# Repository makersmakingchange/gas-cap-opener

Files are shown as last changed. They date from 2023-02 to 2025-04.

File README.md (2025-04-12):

# Gas Cap Opener
The gas cap opener is a device designed to allow users with limited grip strength and hand function to easily open and close the gas cap on their vehicle.

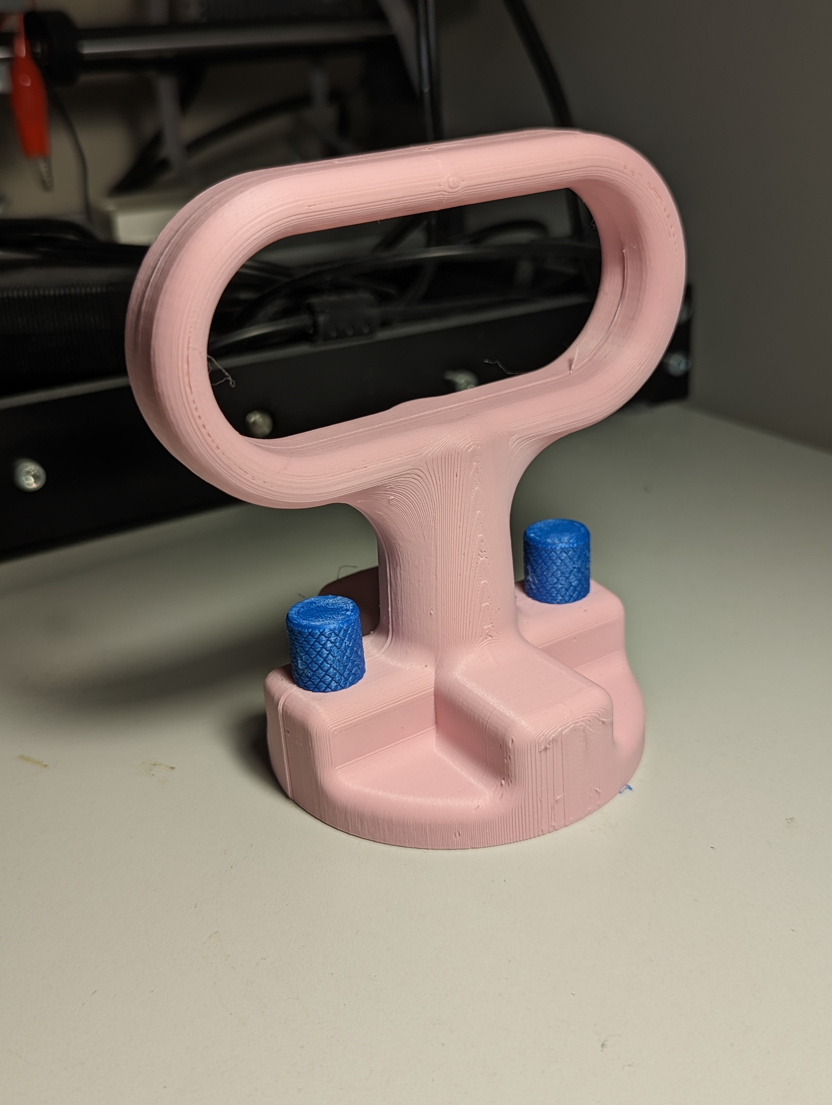
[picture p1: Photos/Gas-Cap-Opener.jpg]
Picture of Gas Cap Opener.


## More info at
- [Makers Making Change Project Page](https://makersmakingchange.com/project/gas-cap-opener/)

## How to Obtain a Gas Cap Opener
### 1. Do it Yourself (DIY) or Do it Together (DIT)

This is an open-source assistive technology, so anyone is free to build it. All of the files and instructions required to build the Gas Cap Opener are contained within this repository. Refer to the Maker Checklist below.

### 2. Request a build of this device

If you would like to obtain a Gas Cap Opener , you may submit a build request through the [MMC Library Page](https://makersmakingchange.com/project/gas-cap-opener/). The requestor is responsible for the cost of materials and any shipping.

### 3. How to build this device for someone else

If you have the skills and equipment to build this device, and would like to donate your time to create the switch for someone who needs it, visit the [MMC Maker Wanted](https://makersmakingchange.com/maker-wanted/) section.

## Getting Started

### 1. Read the Makers Checklist

The Makers Checklist 

### 2. Order the Off-The-Shelf Components

The [Bill of Materials](/Documentation/Gas_Cap_Opener_BOM_V1.0.xlsx) lists all of the parts and components required to build the Gas Cap Opener. 

### 3. Print the 3D Printable components

All of the files and individual print files can be in the [/Build_Files/3D_Printing_Files](/Build_Files/3D_Printing_Files/) folder.

### 4. Assemble the Gas Cap Opener

Reference the [Assembly Guide](/Documentation/Gas_Cap_Opener_Assembly_Guide_V1.0.pdf) for the tools and steps required to build each portion.

## Files
### Documentation
| Document             | Version | Link |
|----------------------|---------|------|
| Design Rationale     | 1.0     | [Gas_Cap_Opener_Design_Rationale](/Documentation/Gas_Cap_Opener_Design_Rationale_V1.0.pdf)     |
| Maker Checklist      | 1.0     | [Gas_Cap_Opener_Maker_Checklist](/Documentation/Gas_Cap_Opener_Maker_Checklist_V1.0.pdf)     |
| Bill of Materials    | 1.0     | [Gas_Cap_Opener_Bill_of_Materials](/Documentation/Gas_Cap_Opener_BOM_V1.0.xlsx)     |
| 3D Printing Guide    | 1.0     | [Gas_Cap_Opener_3D_Printing_Guide](/Documentation/Gas_Cap_Opener_3D_Printing_Guide_V1.0.pdf)     |
| Assembly Guide       | 1.0     | [Gas_Cap_Opener_Assembly_Guide](/Documentation/Gas_Cap_Opener_Assembly_Guide_V1.0.pdf)     |
| User Guide           | 1.0     | [Gas_Cap_Opener_User_Guide](/Documentation/Gas_Cap_Opener_User_Guide_V1.0.pdf)    |
| Changelog            | 1.0     | [Gas_Cap_Opener_Changelog](/Documentation/Gas_Cap_Opener_Changelog_V1.0.pdf)     |

### Design Files
[CAD Files](/Design_Files)

### Build Files
 - [3D Printing Files](/Build_Files/3D_Printing_Files)

## Attribution
Designers:
 - Design and Documentation by Neil Squire Society/Makers Making Change

## License
Everything needed or used to design, make, test, or prepare the Gas Cap Opener is licensed under the [Attribution-NonCommercial-ShareAlike 4.0 ](https://creativecommons.org/licenses/by-nc-sa/4.0/).

Accompanying material such as instruction manuals, videos, and other copyrightable works that are useful but not necessary to design, make, test, or prepare the <Device-Name> are published under a Creative Commons Attribution-ShareAlike 4.0 license https://creativecommons.org/licenses/by-sa/4.0/ (CC BY-SA 4.0).

---
<!-- ABOUT MMC START -->
## About Makers Making Change
[Makers Making Change Logo](https://www.makersmakingchange.com/)

Makers Making Change is a program of [Neil Squire](https://www.neilsquire.ca/), a Canadian non-profit that uses technology, knowledge, and passion to empower people with disabilities.

Makers Making Change leverages the capacity of community based Makers, Disability Professionals and Volunteers to develop and deliver affordable Open Source Assistive Technologies.

 - Website: [www.MakersMakingChange.com](https://www.makersmakingchange.com/)
 - GitHub: [makersmakingchange](https://github.com/makersmakingchange)
 - Bluesky: [@makersmakingchange.bsky.social](https://bsky.app/profile/makersmakingchange.bsky.social)
 - Instagram: [@makersmakingchange](https://www.instagram.com/makersmakingchange)
 - Facebook: [makersmakechange](https://www.facebook.com/makersmakechange)
 - LinkedIn: [Neil Squire Society](https://www.linkedin.com/company/neil-squire-society/)
 - Thingiverse: [makersmakingchange](https://www.thingiverse.com/makersmakingchange/about)
 - Printables: [MakersMakingChange](https://www.printables.com/@MakersMakingChange)

### Contact Us
For technical questions, to get involved, or to share your experience we encourage you to [visit our website](https://www.makersmakingchange.com/) or [contact us](https://www.makersmakingchange.com/s/contact).
<!-- ABOUT MMC END -->

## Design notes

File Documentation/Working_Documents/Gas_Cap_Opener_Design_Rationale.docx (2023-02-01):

# Introduction

Some people with limited grip strength/limited hand function may have difficulty opening the gas cap on their vehicle. There are several commercial and DIY options available for opening vehicle gas caps, but most designs focus on users with limited grip strength, leaving few options available for users with limited hand function.

# Research

Commercial
Name | Picture | Price | Link

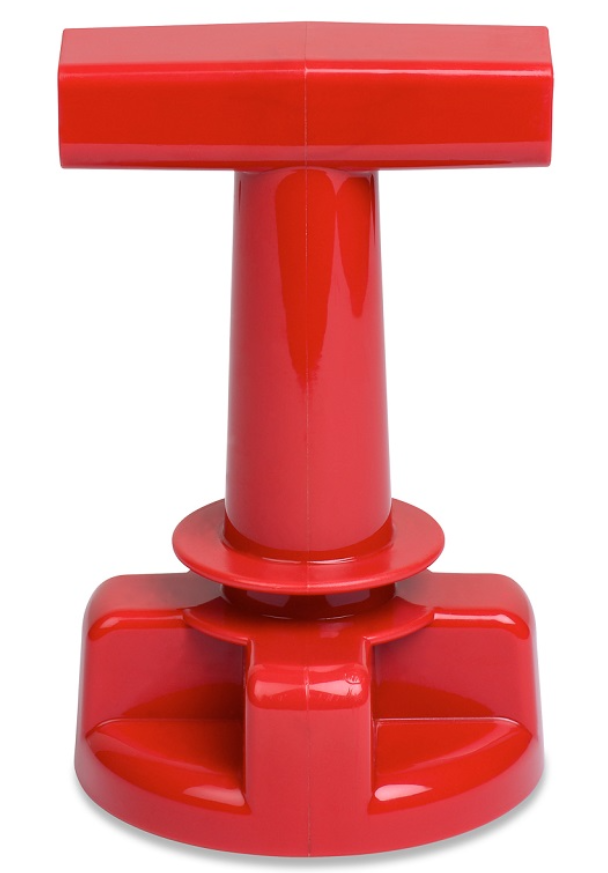
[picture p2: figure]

Freedom Gas Cap Wrench | | $17.95 | Link (https://www.arthritissupplies.com/gas-cap-wrench.html)

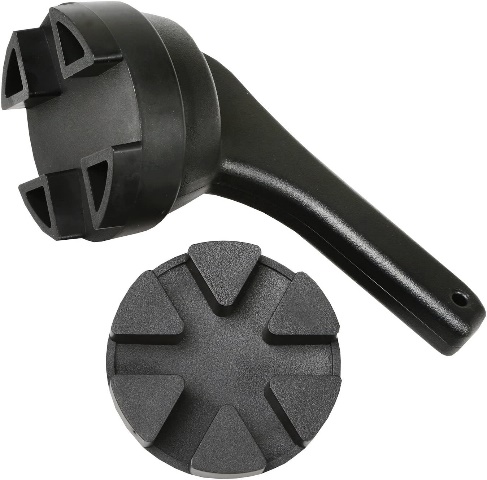
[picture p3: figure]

Bandwagon Gas Cap Aid | | $32.11 | Link (https://www.amazon.ca/BW-BRANDS-9270-Bandwagon-Gas/dp/B072WC9MVF?hvadid=459470168074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)

DIY
Name | Picture | Price | Link

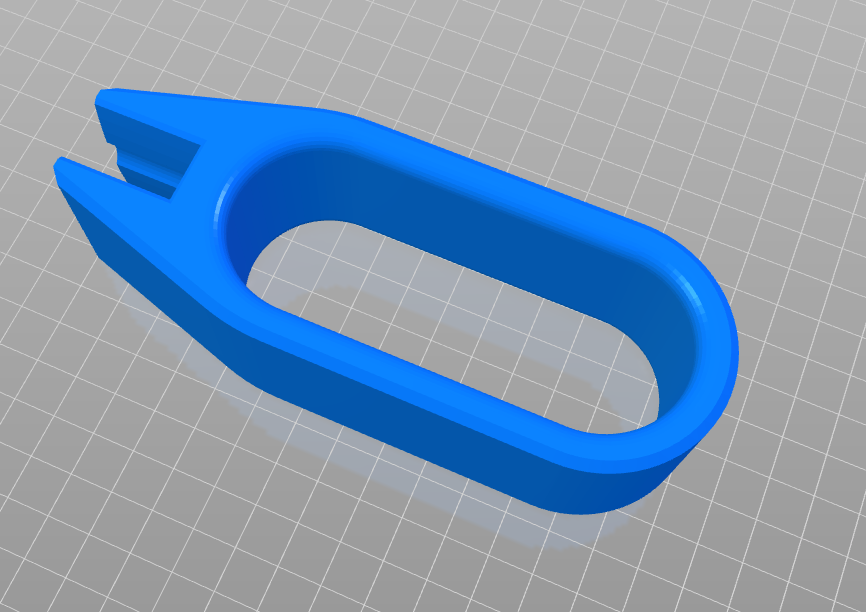
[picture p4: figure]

Gas Cap opener | | N/A | Link (https://www.thingiverse.com/thing:4707409)

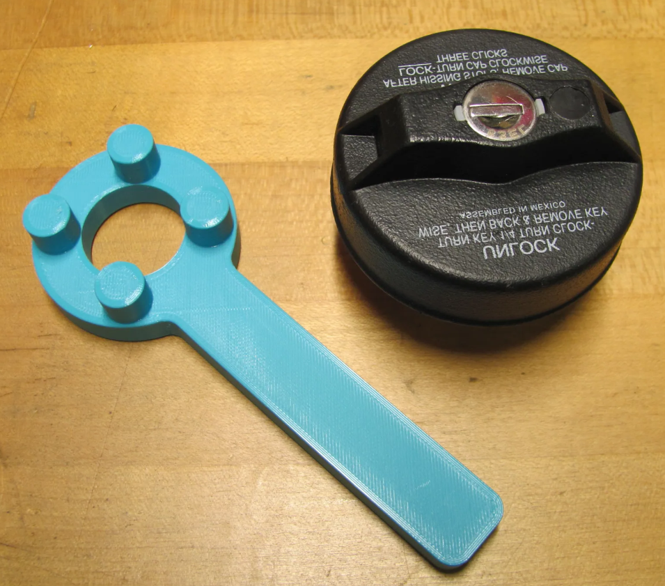
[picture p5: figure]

RV Locking Gas Cap Wrench | | N/A | Link (https://www.printables.com/model/64304-rv-locking-gas-cap-wrench)

# Requirements

## Goals

G01 | To allow users with limited hand function to remove and replace the gas cap on their vehicle

## Functional Requirements

F01 | Device must open and tighten the gas cap on any passenger vehicle
F02 | Device must be usable by users with limited hand function

## Non-functional Requirement

NF01 | Each component printable in less than 8 hours
NF02 | Device must be printable with minimum supports

## Constraints

C01 | Built with 3D printable and off the shelf components

# Prototyping

The initial concept was inspired by the Freedom Gas Cap Wrench. Each round of testing identified a new flaw in the design, and a new prototype was created.

# Testing

The initial prototype was tested on a Toyota Rav4. It removed the gas cap of the vehicle, but the handle was found to be uncomfortable and difficult to grip. Additionally, the bolt attachment points had to be removed for it to fit into the gas cap cavity.

The handle was redesigned along with the new bolt attachment points, and it was tested again on a Rav4 and a Toyota Corolla. This time it was able to remove the gas cap on the Rav4, but it did not fit over the gas cap on the Corolla. The edges were found to catch onto the strap holding the cap to the car.

The width of the gas cap slot was increased for the next prototype, and a chamfer added around the outer ring.

For the final version, the bolts were replaced with 3D printed pins and nuts.

# Opportunities for Improvement

- The device could be redesigned to eliminate printing supports

© 2023 by Neil Squire. This work is licensed under the CC BY SA 4.0 License: http://creativecommons.org/licenses/by-sa/4.0 Files available at https://makersmakingchange.com/project/gas-cap-opener/ Page 2 of 2

V1.0 | January 2023 Gas Cap Opener Design Rationale

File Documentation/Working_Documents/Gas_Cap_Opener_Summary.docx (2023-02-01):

# Title

Gas Cap Opener

## Subtitle

The gas cap opener is a device designed to allow users with limited grip strength and hand function to easily open and close the gas cap on their vehicle.

## Device Details

### Overview

Some people with limited grip strength/hand function have difficulty opening the gas cap on their vehicle. There are several commercial and DIY options available for opening vehicle gas caps, but most focus on grip strength issues, with limited options available for users with limited hand function.

### Usage

To use, place the + shaped end of the gas cap opener over the gas cap on the car. The handle on the opener can then be turned to either tighten or loosen the cap, as normal.

If this device does not function with the gas cap on your vehicle, please get in touch with us so we can make changes to the design to make it compatible with more vehicles.

### Cost

<$10

### Build Instructions

This device is assembled from two separate halves, connected by an aligning pin and two threaded knobs.

#### Skills Required

- 3D Printing

#### Time Required

- 3D printing time: 884 min
- Assembly Time: 5 min

#### Tools

- 3D Printer
- Pliers

#### Components

- Handle x2
- Knob x2
- Pin x1

#### Attribution

Design by Neil Squire Society/Makers Making Change

Initial prototype inspired by the Freedom Gas Cap Wrench

© 2023 by Neil Squire. This work is licensed under the CC BY SA 4.0 License: http://creativecommons.org/licenses/by-sa/4.0 Files available at https://makersmakingchange.com/project/gas-cap-opener/ Page 2 of 2

V1.0 | January 2023 Gas Cap Opener Summary

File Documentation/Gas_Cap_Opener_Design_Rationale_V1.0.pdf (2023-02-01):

V1.0 | January 2023

## Gas Cap Opener

## DESIGN RATIONALE

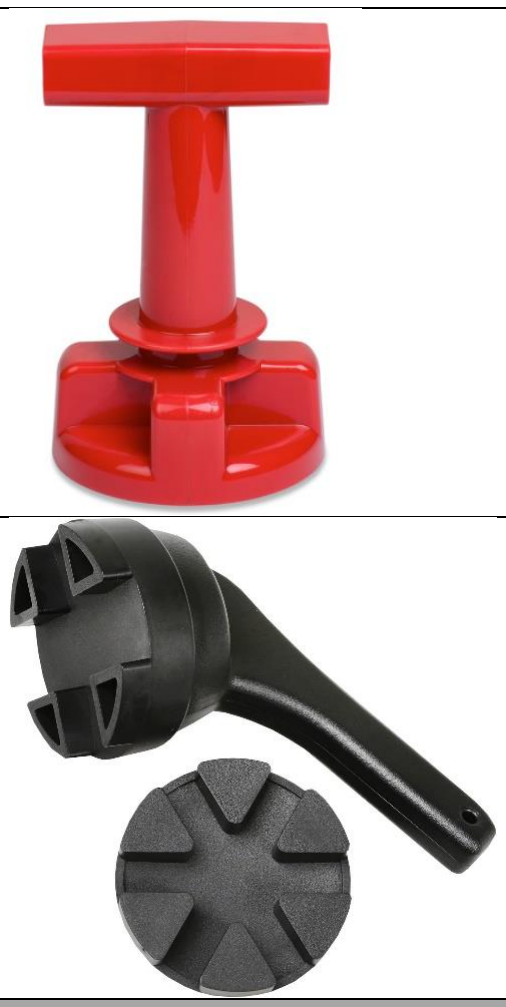
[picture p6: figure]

© 2023 by Neil Squire. (https://neilsquire.ca/)
This work is licensed under the CC BY SA 4.0 License: http://creativecommons.org/licenses/by-sa/4.0
Files available at https://makersmakingchange.com/project/gas-cap-opener/ | Page 1 of 3

### Introduction

Some people with limited grip strength/limited hand function may have difficulty opening the gas cap on their vehicle. There are several commercial and DIY options available for opening vehicle gas caps, but most designs focus on users with limited grip strength, leaving few options available for users with limited hand function.

### Research

Commercial
Name | Picture | Price | Link
Freedom Gas Cap Wrench | | $17.95 | Link (https://www.arthritissupplies.com/gas-cap-wrench.html)
Bandwagon Gas Cap Aid | | $32.11 | Link (https://www.amazon.ca/BW-BRANDS-9270-Bandwagon-Gas/dp/B072WC9MVF?hvadid=459470168074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)

DIY
Name | Picture | Price | Link

## DESIGN RATIONALE

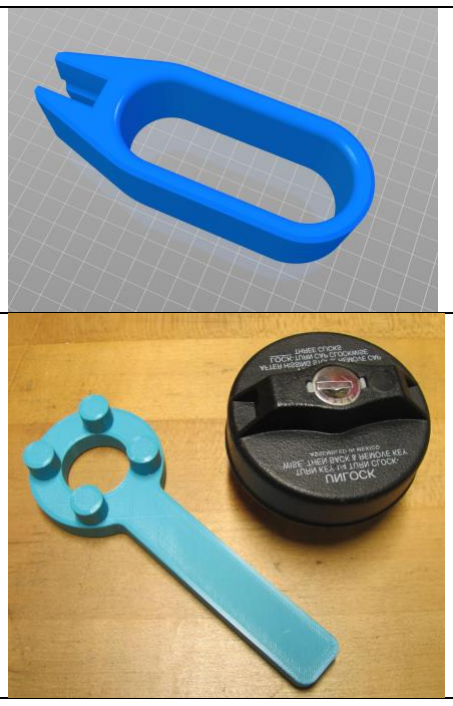
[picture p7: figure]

Files available at https://makersmakingchange.com/project/gas-cap-opener/ | Page 2 of 3
Gas Cap opener | N/A | Link (https://www.thingiverse.com/thing:4707409)
RV Locking Gas Cap Wrench | N/A | Link (https://www.printables.com/model/64304-rv-locking-gas-cap-wrench)

### Requirements

### Goals

G01 To allow users with limited hand function to remove and replace the gas cap on their vehicle

### Functional Requirements

F01 | Device must open and tighten the gas cap on any passenger vehicle
F02 | Device must be usable by users with limited hand function

### Non-functional Requirement

NF01 | Each component printable in less than 8 hours
NF02 | Device must be printable with minimum supports

### Constraints

C01 Built with 3D printable and off the shelf components

## DESIGN RATIONALE

Files available at https://makersmakingchange.com/project/gas-cap-opener/ | Page 3 of 3

### Prototyping

The initial concept was inspired by the Freedom Gas Cap Wrench. Each round of testing identified a new flaw in the design, and a new prototype was created.

### Testing

The initial prototype was tested on a Toyota Rav4. It removed the gas cap of the vehicle, but the handle was found to be uncomfortable and difficult to grip. Additionally, the bolt attachment points had to be removed for it to fit into the gas cap cavity.

The handle was redesigned along with the new bolt attachment points, and it was tested again on a Rav4 and a Toyota Corolla. This time it was able to remove the gas cap on the Rav4, but it did not fit over the gas cap on the Corolla. The edges were found to catch onto the strap holding the cap to the car.

The width of the gas cap slot was increased for the next prototype, and a chamfer added around the outer ring.

For the final version, the bolts were replaced with 3D printed pins and nuts.

### Opportunities for Improvement

- The device could be redesigned to eliminate printing supports

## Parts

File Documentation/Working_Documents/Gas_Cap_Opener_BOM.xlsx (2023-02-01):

Device: Gas Cap Opener |  | Total Cost | Total Print time (hr) | Total filament (g)
Version: V1.0 | Date Created: 1/10/2023 | $2.48 | 7.57 | 99
Commercial Parts:
Part type (Electrical. Mechanical, Sanitization, ect) | Part Name | Quantity Needed | Pkg Quantity | Price per package | Price per Unit | Price for qty needed | Link
 |  |  |  |  |  | $0.00 | https://www.homedepot.ca/product/paulin-1-4-x-1-inch-flat-head-square-drive-stove-bolt-with-nut-zinc-plated-10-pcs/1000122118
 |  |  |  |  |  | $0.00 | https://www.homedepot.ca/product/paulin-1-4-20-inch-finished-hex-nut-grade-2-oversized-hot-dipped-galvanized-unc/1000141150
3D Printed Parts ESTIMATED PRICING USING 1KG ROLL COST: | $25.00
Part | Description | Quantity Needed | TOTAL Mass (g) | Estimated Price | Print Time (Min) | Link
Handle | Main handle body | 2 | 94 | $2.35 | 424
Knob | Threaded knob | 2 | 4 | $0.10 | 20
Pin | Aligning pin | 1 | 1 | $0.03 | 10
 |  |  |  | $0.00
 |  |  |  | $0.00
 |  |  | Total Print Cost: | $2.48
Tools for Assembly
Pliers
Alternatives (if there are other sources for some parts link them below)
Part and description | Link

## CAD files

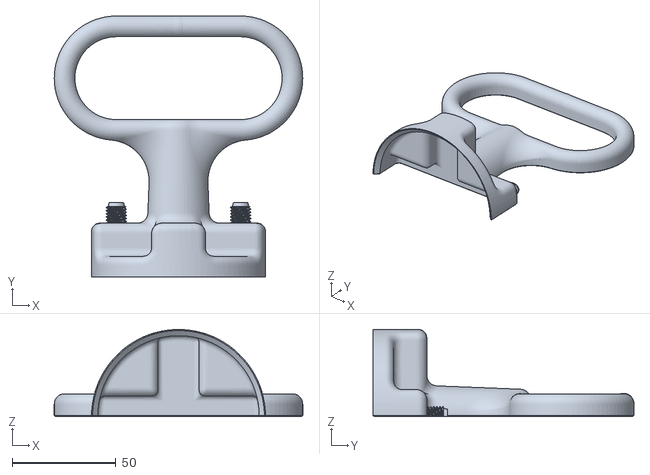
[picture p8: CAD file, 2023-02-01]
Build_Files/3D_Printing_Files/Handle.stl
120.0 x 126.0 x 42.0

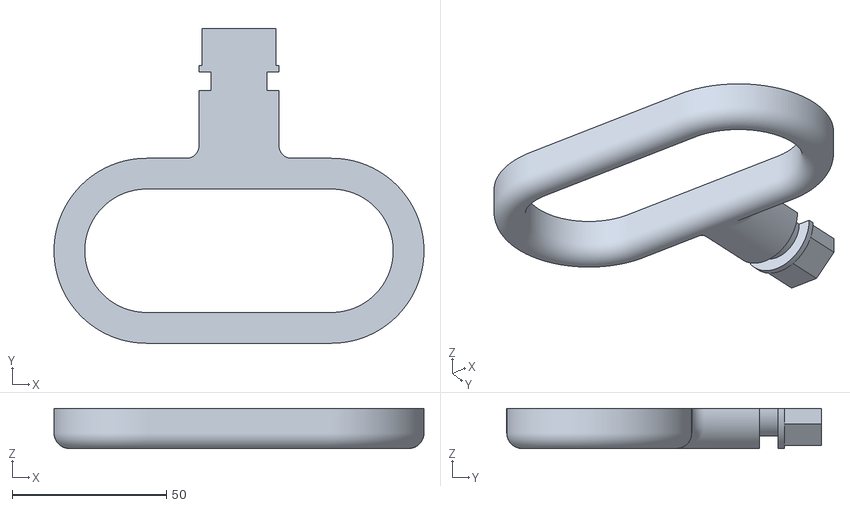
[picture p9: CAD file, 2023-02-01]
Threaded_Variant/Gas_Cap_Opener_Thread_Gas_Cap_Opener_Thread v3_Handle_1_Handle1.stl
120.0 x 102.0 x 13.0

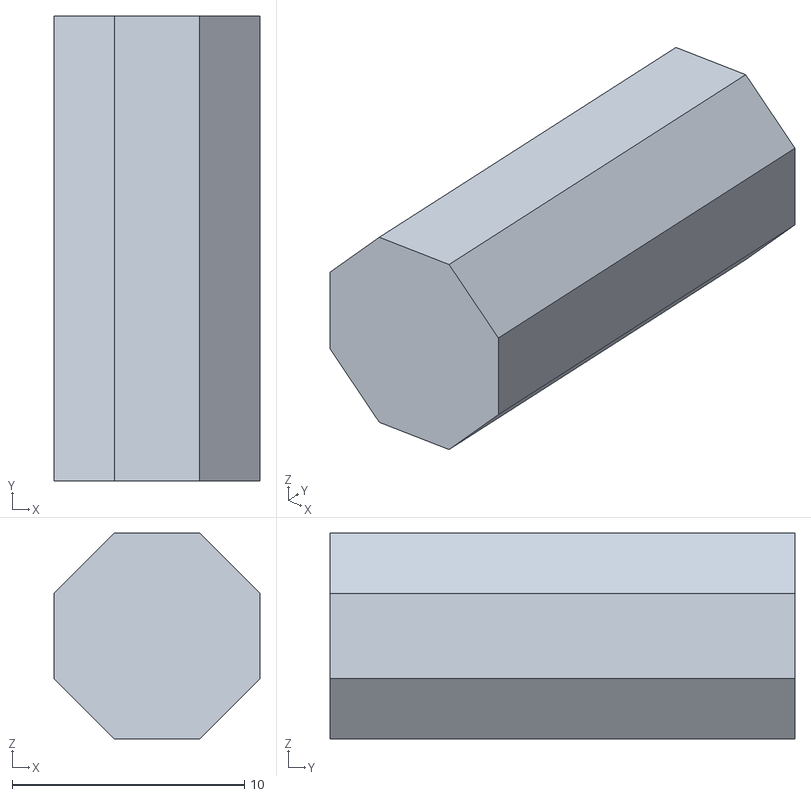
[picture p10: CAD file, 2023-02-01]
Build_Files/3D_Printing_Files/Pin.stl
8.87 x 20.0 x 8.87

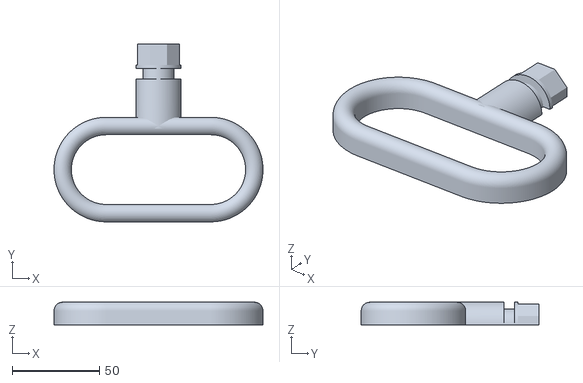
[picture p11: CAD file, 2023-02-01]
Threaded_Variant/Gas_Cap_Opener_Thread_Gas_Cap_Opener_Thread v1_Handle_1_Handle2.stl
120.0 x 102.0 x 13.0

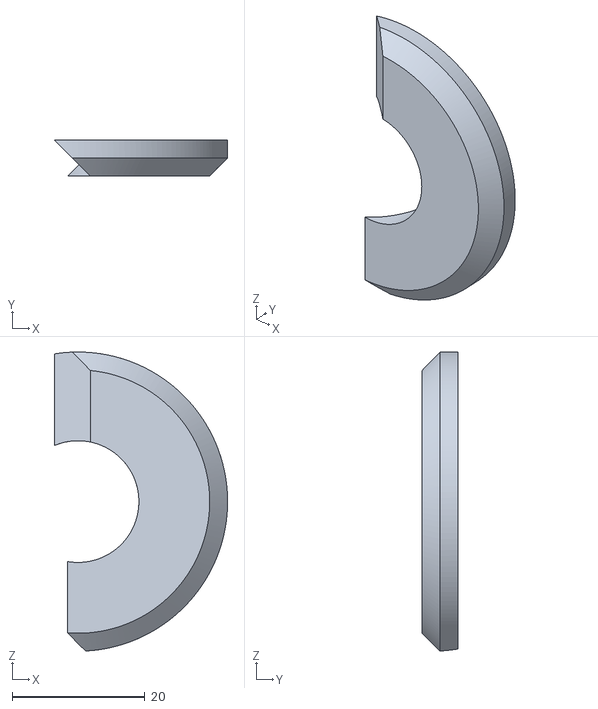
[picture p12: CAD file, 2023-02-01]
Threaded_Variant/Gas_Cap_Opener_Thread_Gas_Cap_Opener_Thread v1_Component6_1_Clip2.stl
26.1 x 5.40 x 45.0

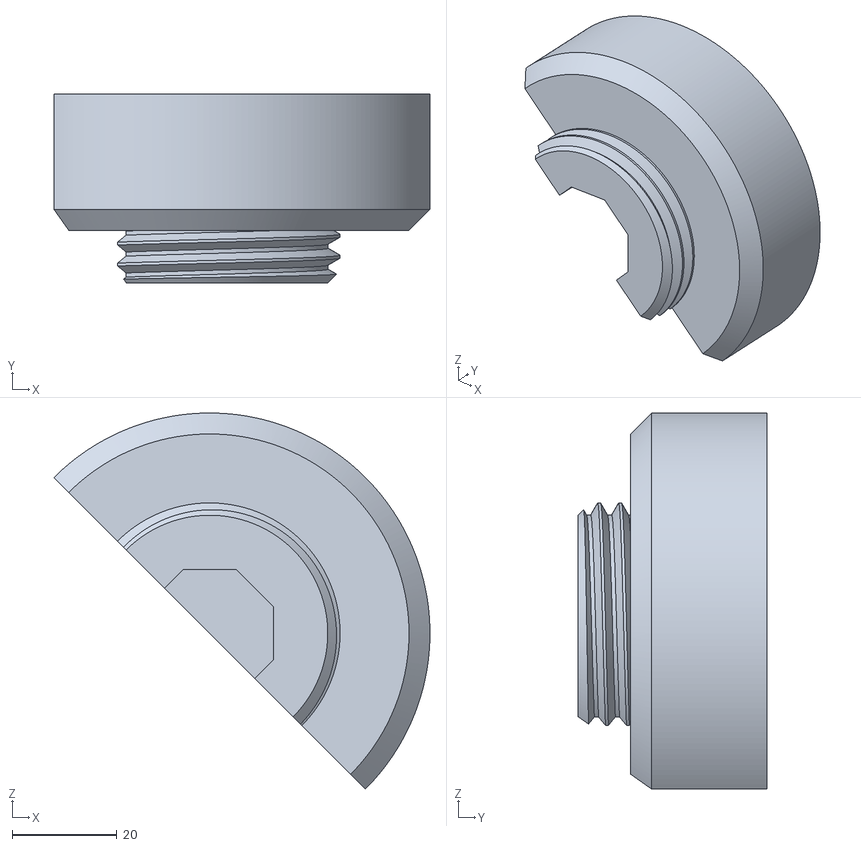
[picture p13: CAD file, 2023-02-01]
Threaded_Variant/Gas_Cap_Opener_Thread_Gas_Cap_Opener_Thread v3_Cap2.stl
71.7 x 36.0 x 71.7

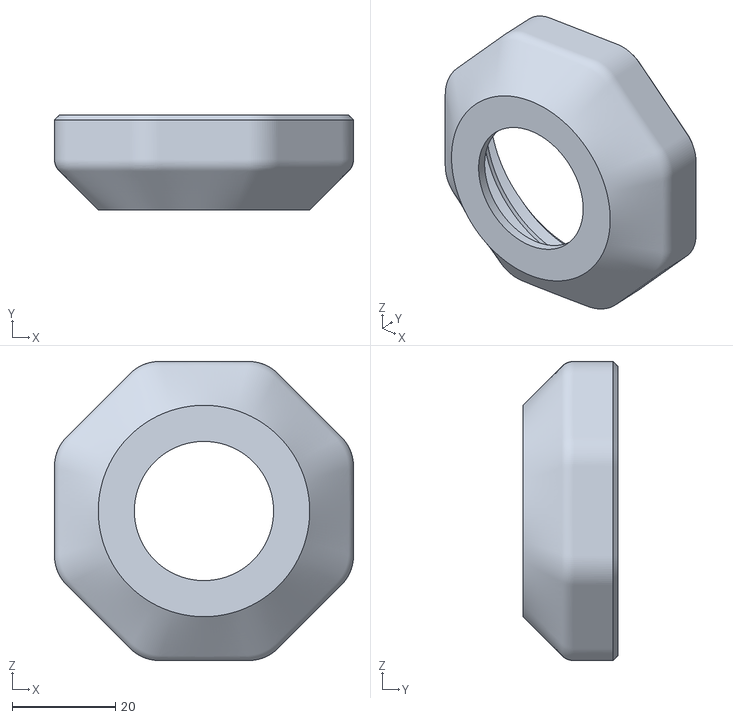
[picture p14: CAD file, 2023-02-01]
Threaded_Variant/Gas_Cap_Opener_Thread_Gas_Cap_Opener_Thread v3_Nut_1_Nut.stl
58.0 x 18.5 x 58.0

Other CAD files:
Threaded_Variant/Gas_Cap_Opener_Thread_Gas_Cap_Opener_Thread v1_Cap2.stl
Threaded_Variant/Gas_Cap_Opener_Thread_Gas_Cap_Opener_Thread v1_Handle_1_Handle1.stl
Threaded_Variant/Gas_Cap_Opener_Thread_Gas_Cap_Opener_Thread v1_Component5_1_Clip1.stl
Threaded_Variant/Gas_Cap_Opener_Thread_Gas_Cap_Opener_Thread v3_Cap1.stl
Threaded_Variant/Gas_Cap_Opener_Thread_Gas_Cap_Opener_Thread v1_Cap1.stl
Threaded_Variant/Gas_Cap_Opener_Thread_Gas_Cap_Opener_Thread v3_Component5_1_Clip1.stl
Threaded_Variant/Gas_Cap_Opener_Thread_Gas_Cap_Opener_Thread v3_Handle_1_Handle2.stl
Design_Files/Gas Cap Opener Finalized v4.f3d

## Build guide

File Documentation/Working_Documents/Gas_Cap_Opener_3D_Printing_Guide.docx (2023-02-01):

# 3D Printing Summary

Metrics | Configuration 1
Total Print Time (min) | 884
Total Number of Components | 5
Typical Total Mass (g) | 99
Typical Number of Print Setups | 3

# 3D Printing Settings

Print File Name | Qty | Total Print Time (hr:min) | Mass (g) | Infill (%) | Support(Y/N) | Layer Height/ Nozzle Diameter(mm) | Notes (orientation, special settings, etc.)
Handle.stl | 2 | 6:32 | 47 | 20 | Y | 0.2/0.4 | - Requires support - Print in orientation given in STL
Knob.stl | 2 | 0:20 | 2 | 20 | N | 0.2/0.4 | - Print in orientation given in STL
Pin.stl | 1 | 0:10 | 1 | 20 | N | 0.2/0.4 | - Print in orientation given in STL

# Customization Options

- The device can be printed in any colour that the user wants

# Post-Processing

- Remove all supports from the handle pieces
- Use a hobby knife and sandpaper to remove any rough edges

# Examples of Quality Prints

Photos of Handle

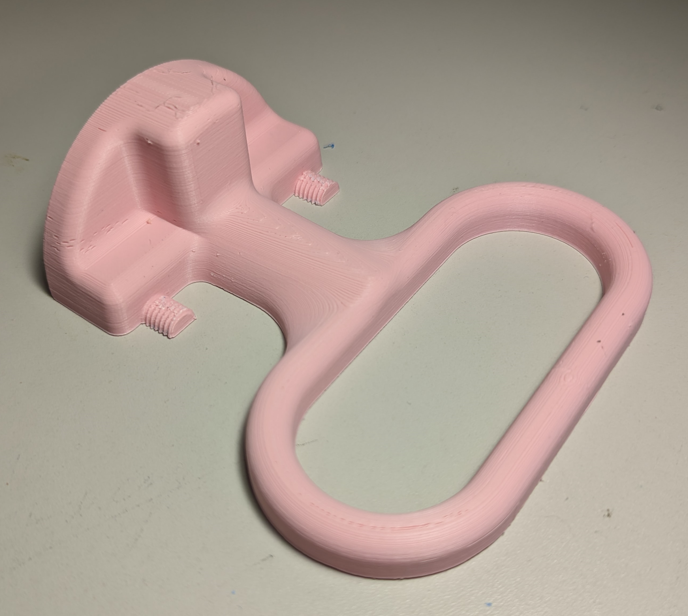
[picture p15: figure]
Top view of handle
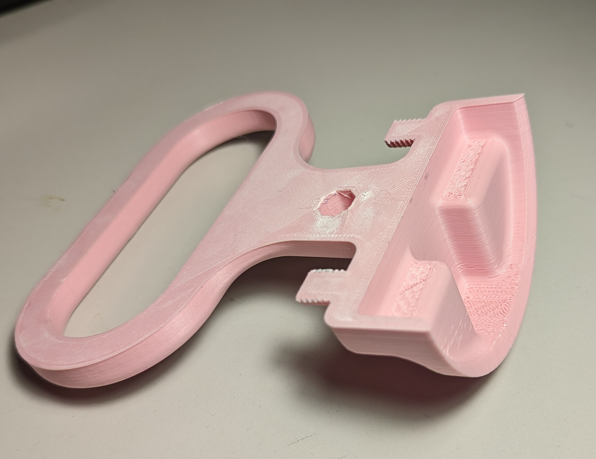
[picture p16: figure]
Bottom view of handle

Photos of Knob

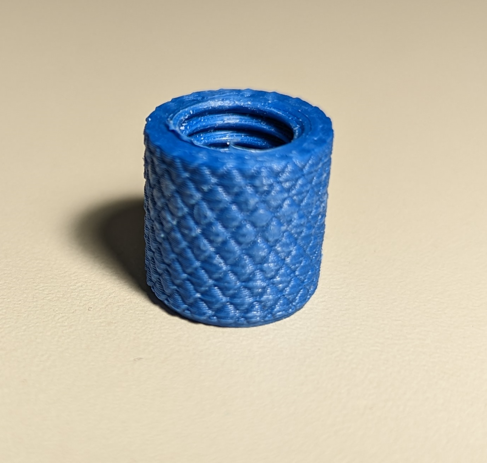
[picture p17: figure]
knob

Photos of Pin

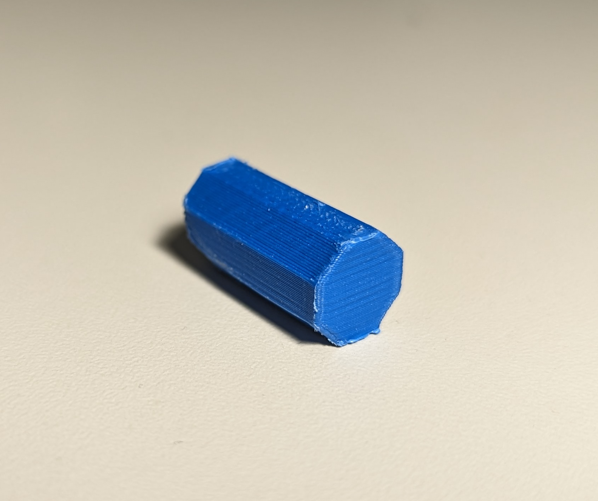
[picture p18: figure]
Octagonal pin

© 2023 by Neil Squire. This work is licensed under the CC BY SA 4.0 License: http://creativecommons.org/licenses/by-sa/4.0 Files available at https://makersmakingchange.com/project/gas-cap-opener/ Page 2 of 2

V1.0 | January 2023 Gas Cap Opener 3D Printing Guide

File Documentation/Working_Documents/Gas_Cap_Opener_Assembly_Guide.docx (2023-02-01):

# Required Components

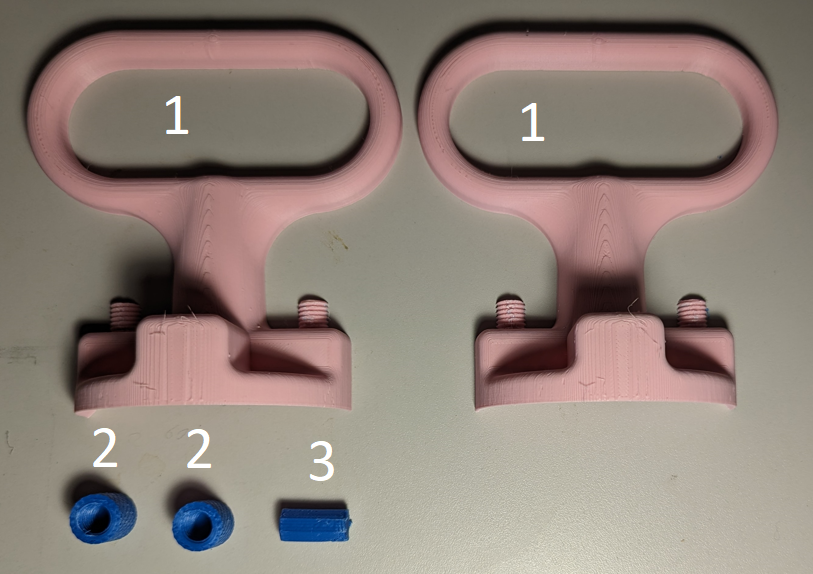
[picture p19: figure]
All the parts for the Gas Cap Opener laid out and numbered

| BOM 1. Handle X2 2. Knob X2 3. Pin

# Required Tools

- Pliers

# Required Personal Protective Equipment (PPE)

- Eye protection

# Assembly Instructions

## Step 1

Insert the octagonal pin into matching slot on one side of the handle.

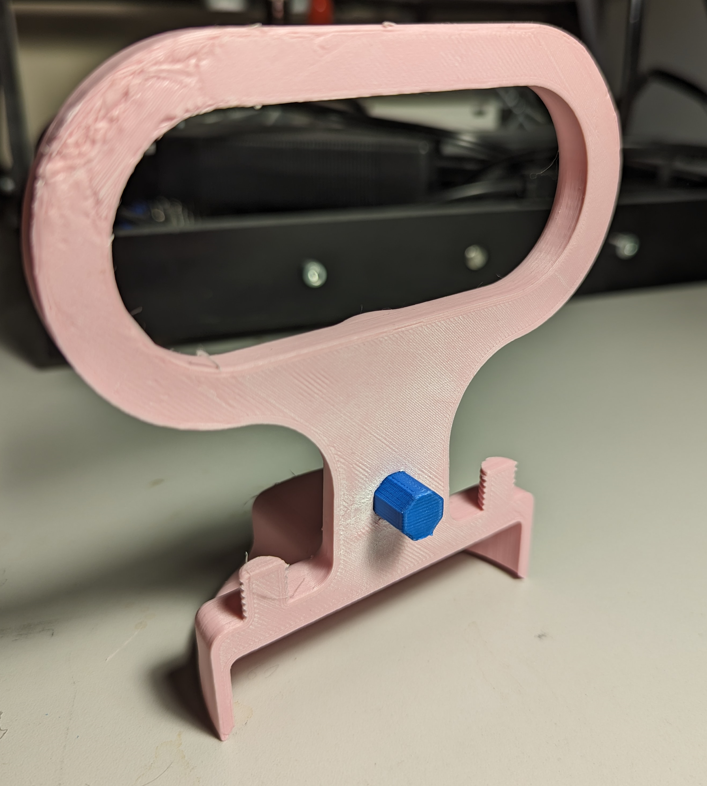
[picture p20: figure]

## Step 2

Align the octagonal hole on the second handle with the pin and press them together.

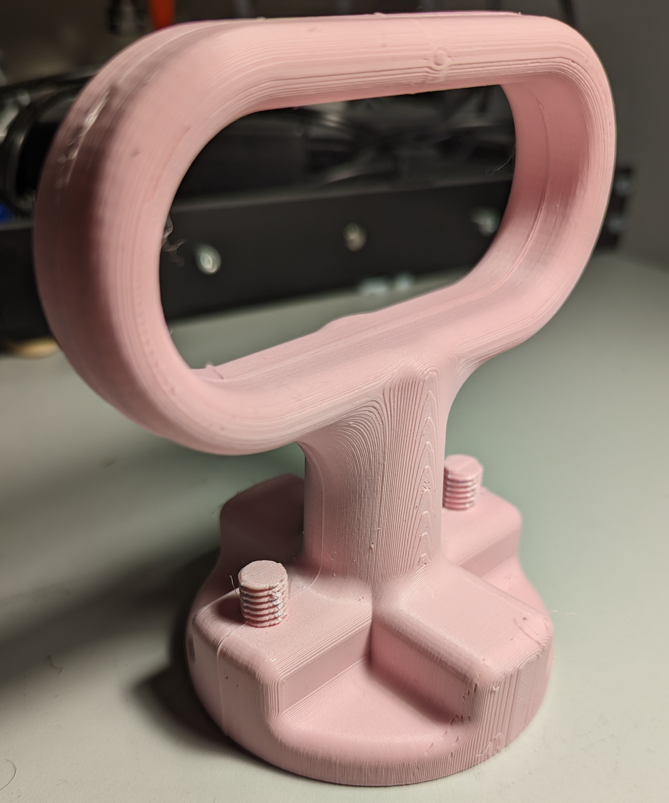
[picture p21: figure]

## Step 3

Screw the knobs onto the threads on the handle. You may need to twist the handle slightly to align the threads. The knob will be tight, and a pair of pliers can be used to fully tighten them.

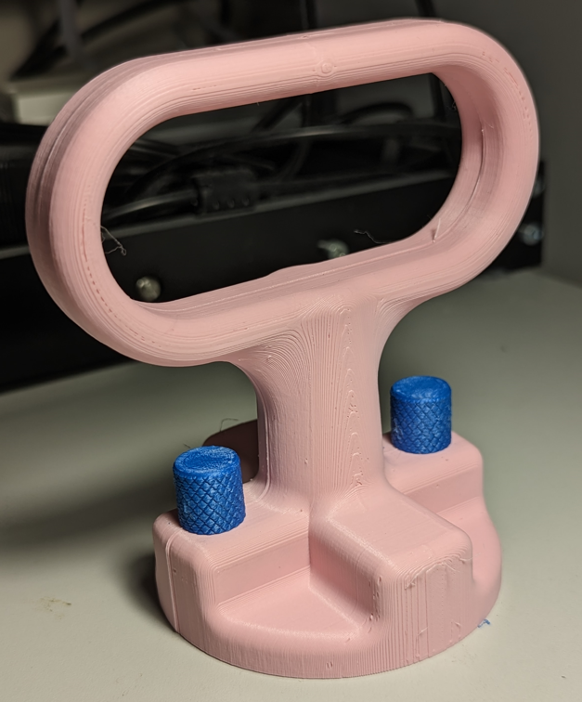
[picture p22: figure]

© 2023 by Neil Squire. This work is licensed under the CC BY SA 4.0 License: http://creativecommons.org/licenses/by-sa/4.0 Files available at https://makersmakingchange.com/project/gas-cap-opener/ Page 2 of 2

V1.0 | January 2023 Gas Cap Opener Assembly Guide

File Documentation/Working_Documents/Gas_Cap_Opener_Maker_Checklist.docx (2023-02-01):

# Maker To Do List

- Read through the Assembly Guide to become familiar with required components, tools, supplies, and safety gear and overall assembly steps.
- Talk to User about customization options (e.g., color, any special requests, etc.)
- Order hardware components
- Gather tools, supplies, and safety equipment.
- Assemble the device
- Test device
- Print “User Quick Guide”

# Items to Give to User

- Assembled, tested device
- “User Quick Guide”

© 2023 by Neil Squire. This work is licensed under the CC BY SA 4.0 License: http://creativecommons.org/licenses/by-sa/4.0 Files available at https://makersmakingchange.com/project/gas-cap-opener/ Page 2 of 2

V1.0 | January 2023 Gas Cap Opener Maker Checklist

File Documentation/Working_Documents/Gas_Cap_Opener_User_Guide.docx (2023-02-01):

## Introduction

Some people with limited grip strength/limited hand function have difficulty opening the gas cap on their vehicle. There are several commercial and DIY options available for opening vehicle gas caps, but most focus on grip strength issues, with limited options available for users with limited hand function.

## Features

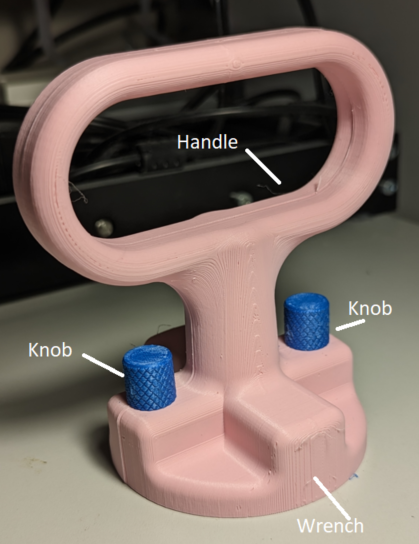
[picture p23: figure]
Annotated picture of the wrench

## Usage

To use, place the + shaped end of the gas cap opener over the gas cap on the car. The handle on the opener can then be turned to either tighten or loosen the cap, as normal.

## Compatibility

The gas cap opener is compatible with every gas cap with a handle width of less than 2cm and a length of less than 8cm.

## Specifications

The handle is 5cm by 10cm, the overall device is 12.5cm tall, and has a wrench diameter of 8.5 cm.

The device weighs 70g

## Cleaning

Wipe device clean with damp cloth.

© 2023 by Neil Squire. This work is licensed under the CC BY SA 4.0 License: http://creativecommons.org/licenses/by-sa/4.0 Files available at https://makersmakingchange.com/project/gas-cap-opener/ Page 2 of 3

V1.0 | January 2023 Gas Cap Opener user Quick Guide

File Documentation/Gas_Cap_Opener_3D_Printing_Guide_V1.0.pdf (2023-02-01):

V1.0 | January 2023

## Gas Cap Opener

## 3D PRINTING GUIDE

© 2023 by Neil Squire. (https://neilsquire.ca/)
This work is licensed under the CC BY SA 4.0 License: http://creativecommons.org/licenses/by-sa/4.0
Files available at https://makersmakingchange.com/project/gas-cap-opener/ | Page 1 of 3

### 3D Printing Summary

Metrics | Configuration 1
Total Print Time (min) | 884
Total Number of Components | 5
Typical Total Mass (g) | 99
Typical Number of Print Setups | 3

### 3D Printing Settings

Print File Name | Qty | Total Print Time (hr:min) | Mass (g) | Infill (%) | Support(Y/N) | Layer Height/ Nozzle Diameter(mm) | Notes (orientation, special settings, etc.)
Handle.stl | 2 | 6:32 | 47 | 20 | Y | 0.2/0.4 | -Requires support - Print in orientation given in STL
Knob.stl | 2 | 0:20 | 2 | 20 | N | 0.2/0.4 | -Print in orientation given in STL
Pin.stl | 1 | 0:10 | 1 | 20 | N | 0.2/0.4 | -Print in orientation given in STL

### Customization Options

- The device can be printed in any colour that the user wants

### Post-Processing

- Remove all supports from the handle pieces
- Use a hobby knife and sandpaper to remove any rough edges

## 3D PRINTING GUIDE

### Examples of Quality Prints

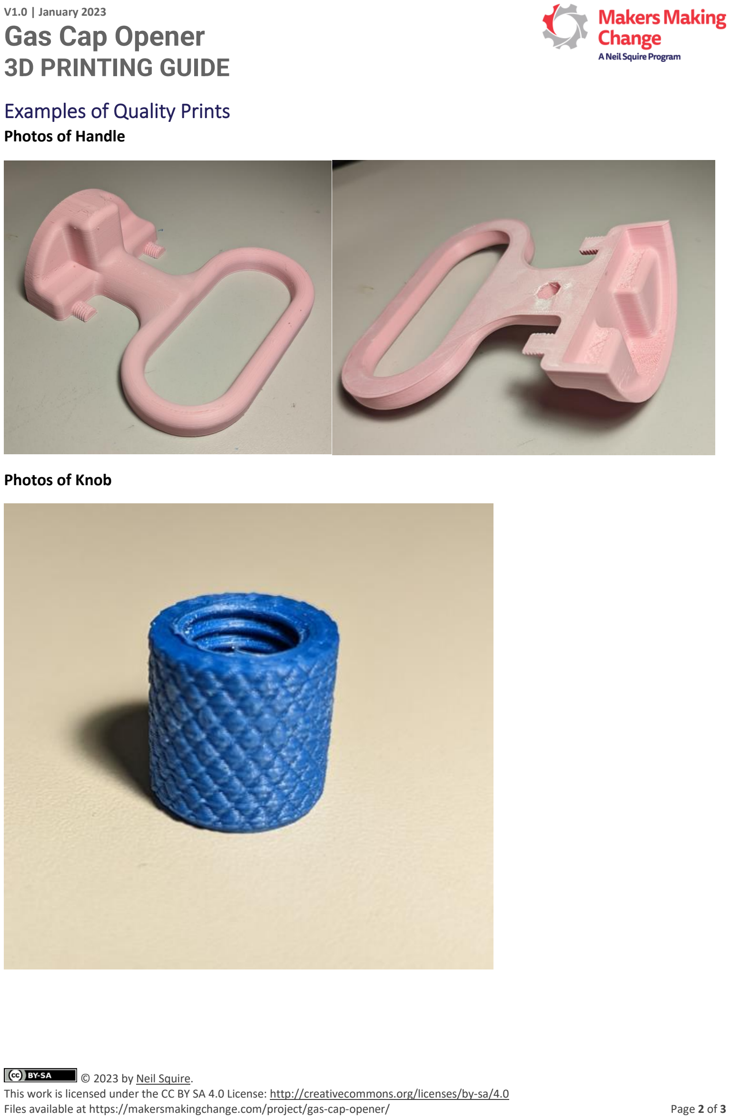
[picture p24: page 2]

Files available at https://makersmakingchange.com/project/gas-cap-opener/ | Page 2 of 3

Photos of Handle

Photos of Knob

## 3D PRINTING GUIDE

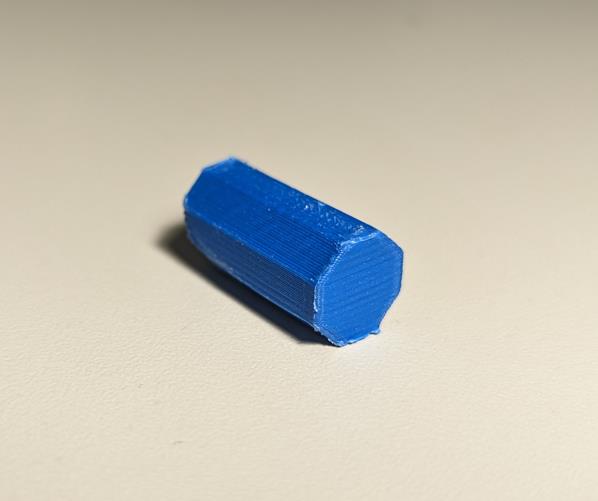
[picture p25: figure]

Files available at https://makersmakingchange.com/project/gas-cap-opener/ | Page 3 of 3

Photos of Pin

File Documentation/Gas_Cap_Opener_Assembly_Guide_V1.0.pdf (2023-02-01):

V1.0 | January 2023

# Gas Cap Opener

# ASSEMBLY GUIDE

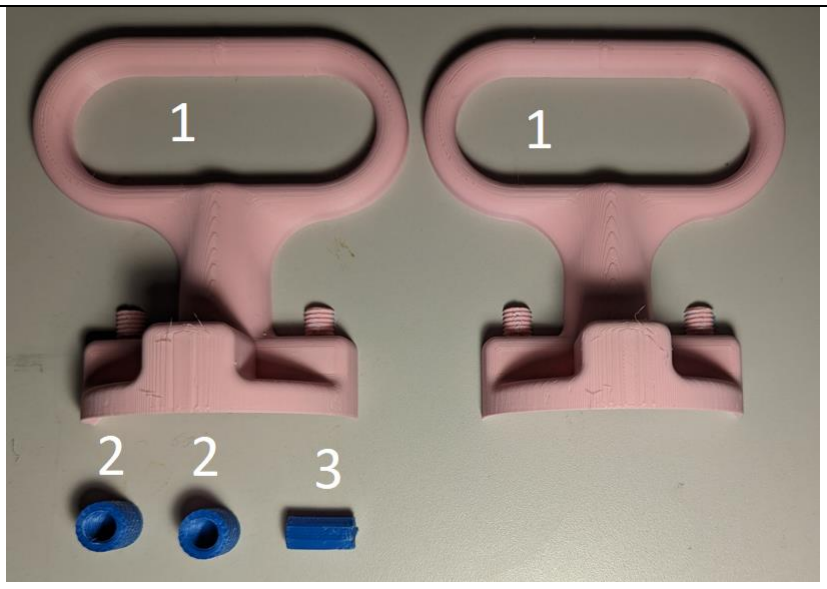
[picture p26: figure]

© 2023 by Neil Squire. (https://neilsquire.ca/)
This work is licensed under the CC BY SA 4.0 License: http://creativecommons.org/licenses/by-sa/4.0
Files available at https://makersmakingchange.com/project/gas-cap-opener/ | Page 1 of 4

# Required Components

## BOM 1. Handle X2 2. Knob X2 3. Pin

# Required Tools

## - Pliers

# Required Personal Protective Equipment (PPE)

## - Eye protection

# ASSEMBLY GUIDE

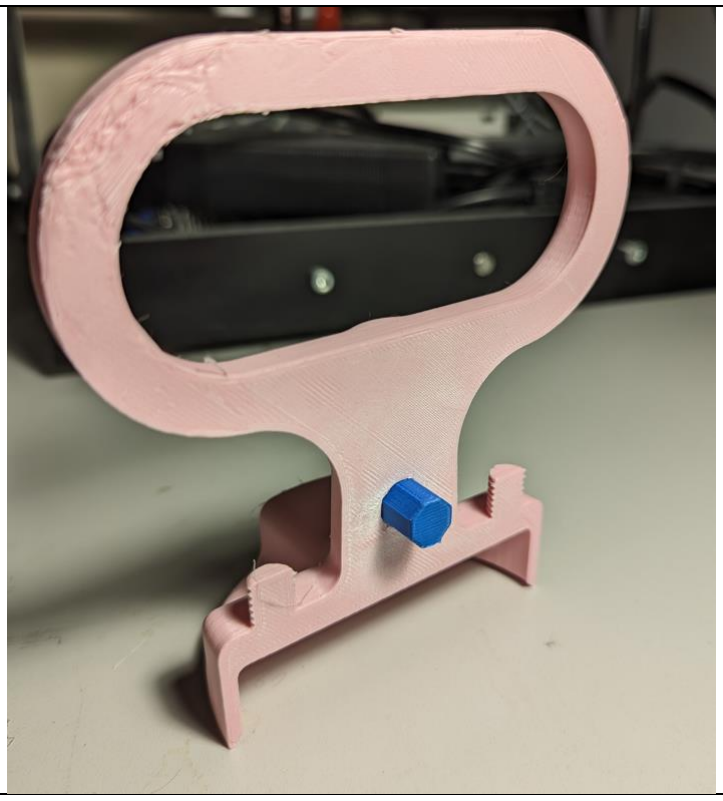
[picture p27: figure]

Files available at https://makersmakingchange.com/project/gas-cap-opener/ | Page 2 of 4

# Assembly Instructions

## Step 1

Insert the octagonal pin into matching slot on one side of the handle.

# ASSEMBLY GUIDE

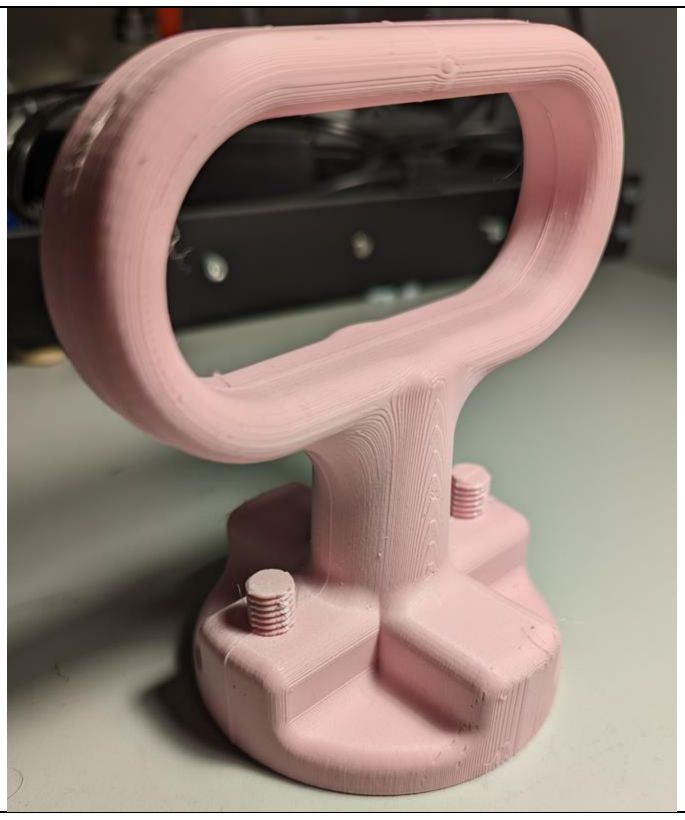
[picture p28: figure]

Files available at https://makersmakingchange.com/project/gas-cap-opener/ | Page 3 of 4

## Step 2

Align the octagonal hole on the second handle with the pin and press them together.

# ASSEMBLY GUIDE

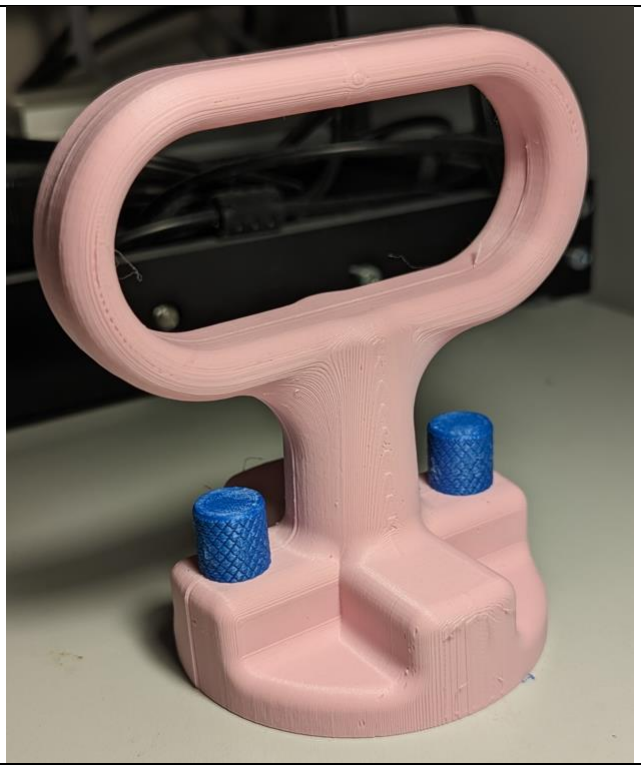
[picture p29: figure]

Files available at https://makersmakingchange.com/project/gas-cap-opener/ | Page 4 of 4

## Step 3

Screw the knobs onto the threads on the handle. You may need to twist the handle slightly to align the threads. The knob will be tight, and a pair of pliers can be used to fully tighten them.

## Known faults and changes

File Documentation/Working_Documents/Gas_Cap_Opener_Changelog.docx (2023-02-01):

# Version 1.0 | 2023/01/12

- Design: Neil Squire / Makers Making Change
- Documentation: Neil Squire / Makers Making Change

© 2023 by Neil Squire. This work is licensed under the CC BY SA 4.0 License: http://creativecommons.org/licenses/by-sa/4.0 Files available at https://makersmakingchange.com/project/gas-cap-opener/ Page 2 of 2

V1.0 | January 2023 Gas Cap Opener changelog
